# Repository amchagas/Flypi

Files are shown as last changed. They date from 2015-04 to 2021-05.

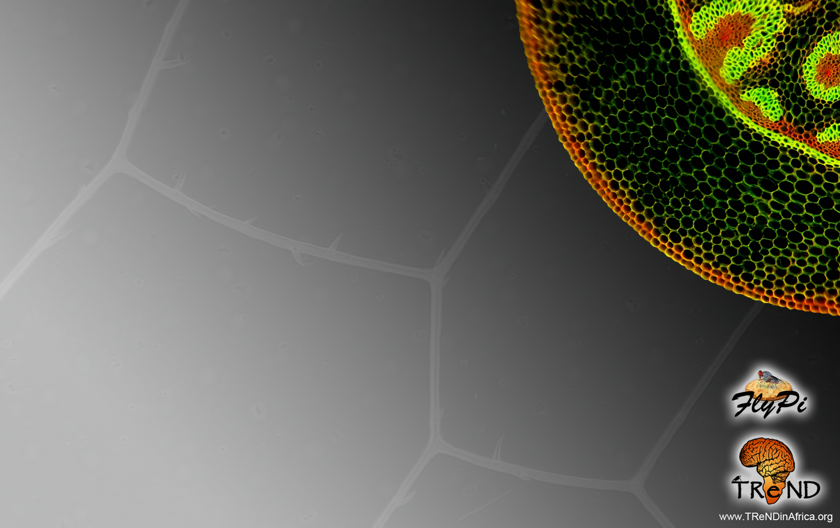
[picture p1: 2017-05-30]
logos/FlyPi_background.png

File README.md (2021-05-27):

#### Flypi - An open source, modular, affordable tool for imaging experiments.

[]()

[]()

Hi! Thanks for dropping by. This project started during one of the summer courses organized by [Trend in Africa](www.trendinafrica.org). It developed to the current state due to the efforts of many people along the way. In special Tom Baden, Lucia Prieto, and Edwin Cruz. A paper describing the system was published in [Plos Biology](http://journals.plos.org/plosbiology/article?id=10.1371/journal.pbio.2002702).

 Version 1.0 was released with the paper and can be found [here](https://github.com/amchagas/Flypi/tree/v1.0.0).

The system can be used for optical microscopy, fluorescence, behavioural tracking, optogenetics, calcium imaging and thermogenetics (see examples recorded with the system below).

#### Some samples imaged with the device:

| C.Elegans behaviour    | Drosophila Crimson  |Fluorescence ZebraFish GFP expressed in heart tissue    |
|---|---|---|
|  GCamP_ZebraFish  |Zebra Fish Transmission   |  Drosophila walking about  |

### Custom PCB

You can order the PCBs and buy the parts to assemble them through the [Kitspace page](https://kitspace.org/boards/github.com/prometheus-science/FlyPi).

#### Necessary Libraries:

LED Ring from Adafruit:
https://github.com/adafruit/Adafruit_NeoPixel

LED Matrix from Adafruit:
https://github.com/adafruit/Adafruit-LED-Backpack-Library

gpac library:
sudo apt-get update
sudo apt-get install gpac

## *.h264 conversion to *.avi:
Done via gpac. MP4BOX.

## Zipped SD Card image containing Raspian image with all things installed:

[IMAGE](https://bit.ly/flyipimg)

## Contributors ✨

Thanks goes to these wonderful people ([emoji key](https://allcontributors.org/docs/en/emoji-key)):

<!-- ALL-CONTRIBUTORS-LIST:START - Do not remove or modify this section -->
<!-- prettier-ignore -->
<table>
  <tr>
    <td align="center"><a href="http://www.openeuroscience.com">Andre Maia Chagas<br /><sub><b>Andre Maia Chagas</b></sub></a><br /><a href="https://github.com/amchagas/Flypi/commits?author=amchagas" title="Code">💻</a> <a href="#design-amchagas" title="Design">🎨</a> <a href="https://github.com/amchagas/Flypi/commits?author=amchagas" title="Documentation">📖</a></td><td align="center"><a href="https://github.com/icaven">icaven<br /><sub><b>icaven</b></sub></a><br /><a href="#design-icaven" title="Design">🎨</a></td>
    <td align="center"><a href="https://github.com/GrandeCappuccino">Edwin Cruz<br /><sub><b>Edwin Cruz</b></sub></a><br /><a href="#design-GrandeCappuccino" title="Design">🎨</a></td><td align="center"><a href="http://www.badenlab.org">Tom Baden<br /><sub><b>Tom Baden</b></sub></a><br /><a href="#design-TomBaden" title="Design">🎨</a> <a href="https://github.com/amchagas/Flypi/commits?author=TomBaden" title="Code">💻</a></td><td align="center"><a href="https://github.com/isobianin">Ihor Sobianin<br /><sub><b>Ihor Sobianin</b></sub></a><br /><a href="#design-isobianin" title="Design">🎨</a></td>
    <td align="center"><a href="https://kitspace.org">Kaspar Emanuel<br /><sub><b>Kaspar Emanuel</b></sub></a><br /><a href="https://github.com/amchagas/Flypi/commits?author=kasbah" title="Code">💻</a></td><td align="center"><a href="https://github.com/ifriad">ifriad<br /><sub><b>ifriad</b></sub></a><br /><a href="#design-ifriad" title="Design">🎨</a> <a href="https://github.com/amchagas/Flypi/commits?author=ifriad" title="Code">💻</a></td>
  </tr>
</table>

<!-- ALL-CONTRIBUTORS-LIST:END -->

This project follows the [all-contributors](https://github.com/all-contributors/all-contributors) specification. Contributions of any kind welcome!

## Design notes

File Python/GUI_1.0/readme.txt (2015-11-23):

The flypi python code is deveped in Python3 and
is now divided in the following manner:

--flypiApp.py is the code that brings different classes together into the GUI

--Run.py takes care of "executing" the flypiApp. It creates a tkinter 
root object, throws it in flypiApp, and takes care of destroying it when the 
program is terminated.

--the other files are responsible for each peripheric device used. So if the 
user wants to create code for a new peripheric device, he/she should start by 
creating a new ".py" file and with a class that contains all code to control 
that device.

---To run this new code, the user should, should call the run.py file, either 
by calling "python3 /complete/path/to/run.py" or by moving into the folder
 where the file is and then calling it from there.

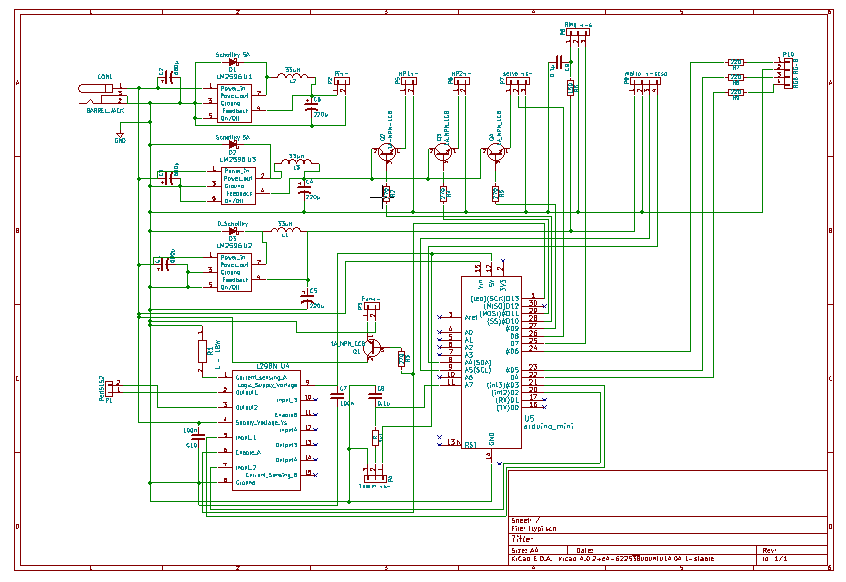
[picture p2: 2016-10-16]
PCB/flypi_pcb_kicad_smd/schematic_view.png

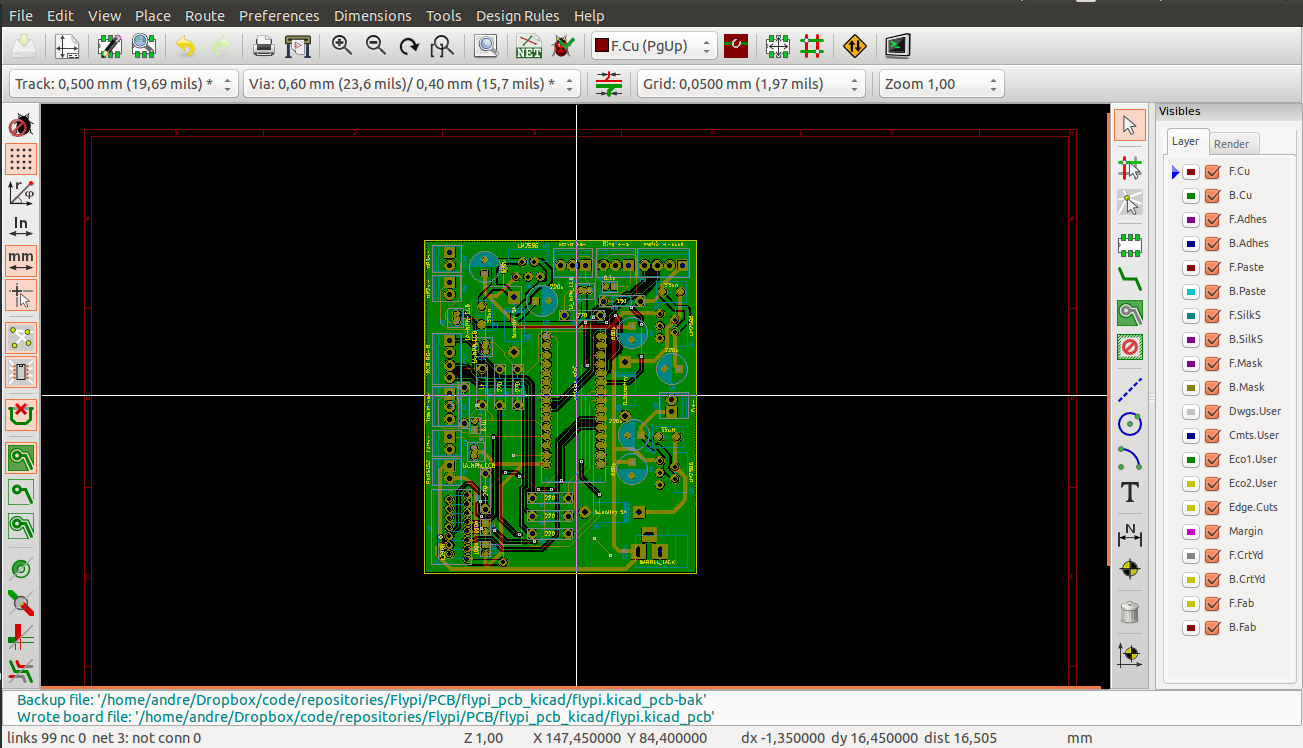
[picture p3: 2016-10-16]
PCB/flypi_pcb_kicad_smd/pcb_view.png

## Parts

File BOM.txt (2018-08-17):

Please find all necessary parts and materials for the FlyPi in: PCB/1-click-bom.tsv

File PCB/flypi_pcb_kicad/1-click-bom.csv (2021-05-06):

References | Qty | Description | Manufacturer | MPN | Manufacturer_1 | MPN_2 | Manufacturer_3 | MPN_4 | Manufacturer_5 | MPN_6 | Manufacturer_7 | MPN_8 | Digikey | Mouser | RS | Newark | Farnell
U5; | 2 | Headers 15 pin 1 row | Samtec inc | SSA-115-S-T | Samtec Inc | SSW-115-01-T-S | Amphenol | 75915-315LF |  |  |  |  | SAM1122-15-ND | 200-SSA115ST | 859-9390 | 11P7739 | 2779587
U4; | 1 | L298N Multiwatt 15 Vertical | STMicroelectronics | L298N |  |  |  |  |  |  |  |  | 497-1395-5-ND | 511L298 | 636384 | 32M1527 | 403295
U1; U2 | 2 | LM2596 5v | ITO-220 | Texas Instruments | Texas Instruments | LM2596T-5.0/NOPB |  |  |  |  |  |  | LM2596T-5.0/NOPB-ND | 926LM2596T5.0/NOPB | 5333743 | 97K3256 | 1150103
R7; R8; R9 | 3 | Resistor 220 ohm 250mW through-hole | Yageo | MFR-25FBF52-220R | TE Connectivity | CBT25J220R | TE Connectivity | CFR16J220R | Ohmite | OD221JE | Stackpole Electronics | CF14JT220R | CF14JT220RCT-ND | 279CBT25J220R | 8066376 | 21R0186 | 1265068
R2; R3; R4; R5 | 4 | Resistor 270 ohm 250mW through-hole | Stackpole Electronics | CF14JT270R | Yageo | MFR-25FBF52-220R | TE Connectivity | CFR16J270R | Ohmite | OD271JE | Kamaya | RC1/4271JB | CF14JT270RCT-ND | 791-RC1/4-271JB | 148360 | 95W5736 | 2329504
R1; | 1 | Resistor 20W TO-220 | Bourns | PWR220T-20-R500F |  |  |  |  |  |  |  |  | PWR220T-20-R500F-ND | 652PWR220T20R500F | 7962508 | 55R1098 | 2328267
Q1; Q2; Q3; Q4; Q1 | 4 | 1A NPN | ON Semiconductor/fairchild | PN2222ATF |  |  |  |  |  |  |  |  | PN2222ATFCT-ND | 512-PN2222ATF | 806-1296 | 31Y3451 | 2453811
P9; | 1 | Header 4 pin 1 row | Sullins | PPTC041LFBN-RC | Amp TE connectivity | 147721-3 |  |  |  |  |  |  | S7002-ND | 571-215297-4 | 4958543 | 98K6514 | 3419060
P10; | 1 | CONN HEADER XH TOP 4POS 2.5MM | JST | B4B-XH-A (LF)(SN) |  |  |  |  |  |  |  |  | 455-2249-ND |  | 820-1551 |  | 1516278
P4; P7; P8; | 3 | CONN HEADER XH TOP 3POS 2.5MM | JST | B3B-XH-A (LF)(SN) |  |  |  |  |  |  |  |  | 455-2248-ND |  | 8201557 | 73M9431 | 1516277
P1; P3; P5; P6; | 4 | CONN HEADER XH TOP 2POS 2.5MM | JST | B2B-XH-A (LF)(SN) |  |  |  |  |  |  |  |  | 455-2247-ND |  | 8201554P | 73M9415 | 1516276
L1; L2; | 2 | INDUCTOR 33µH Neosid MA-Bs75 | Bourns | RLB0914-330KL |  |  |  |  |  |  |  |  | RLB0914-330KL-ND | 652RLB0914330KL | 8118853 | 61J7916 | 2309242
J12; | 1 | USB A Vertical | FCI | 73725-0110BLF | Molex | 48204-0001 |  |  |  |  |  |  | 609-1041-ND | 649737250110BLF | 7710048 | 56R0832 | 2782046
D1; D3; | 2 | Diode Schottky 5A DO-201AD | Vishay | 1N5822-E3/73 | Zetex | SB5100-T |  |  |  |  |  |  | 1N5822-E3/73GICT-ND | 6251N5822E3/73 | 751-4843 | 17T8202 | 1336553
CON1; | 1 | Barrel Jack 2.1mm socket | Cliff | FC68148 DC10A | Lumberg | NEB 21 R | CUI devices | PJ-202AH | Gravitech | CON-SOCJ-2155 | Parallax | 452-00007 | CP-202AH-ND | 992CONSOCJ2155 | 5051609 | 08WX2563 | 224959
C6; C5; | 2 | CAP ALUM 220UF 20% 25V RADIAL | Panasonic | EEU-FM1E221 | Panasonic | ECA-1CM221B | Panasonic | ECE-A0GKS221 | Panasonic | EEU-EB1A221S |  |  | P12383-ND | 667ECA1CM221B | 7472036 | 70K9673 | 9451099
C2; C1; | 2 | 680µF Capacitor | Rubycon | 16ZL680MEFC10X16 | Panasonic | EEU-FC1A681 | Panasonic | EEU-FP1E681 |  |  |  |  | 1189-3978-ND | 667-EEU-FP1E681 | 7037258 | 31M6417 | 1144691
C10; C7; C8; | 3 | 100nF Capacitor Disc | Multicomp | MCFYU6104Z6 | KEMET | C052C104K5R5CA | KEMET | C052K104K5X5CA | KEMET | C052T104K5X5CS | KEMET | C321C104K5R5HA | BC1160CT-ND | 80C321C104K5R5HA | 852-3277 | 73M2154 | 2395773
1k1; | 1 | Resistor 1k 250mW through-hole | Multicomp | MF12 1K | Yageo | MFR-25FBF52-1K | RS Pro | 7077666 |  |  |  |  | 1.00KXBK-ND | 603MFR25FBF521K | 7077666 | 38K5400 | 9342400
MCU; | 1 | Arduino Mini | Arduino | A000087 | Arduino | A000005 |  |  |  |  |  |  | 1050-1001-ND | 992-ARD-NANO30 | 696-1667 | 13T9275 | 1848691
2 pin housing; | 4 | plastic housing for crimped cables 2 pins XH | JST | XHP-2 |  |  |  |  |  |  |  |  | 455-2266-ND |  | 1667314 |  | 1516264
3 pin housing; | 3 | plastic housing for crimped cables 3 pins XH | JST | XHP-3 |  |  |  |  |  |  |  |  | 455-2219-ND | 941-XHP35A0D0BD440E | 8201614 |  | 1516265
4 pin housing; | 1 | plastic housing for crimped cables 4 pins XH | JST | XHP-4 |  |  |  |  |  |  |  |  | 455-2267-ND |  | 1667316 | 74M5179 | 1516266
Crimped cable; | 21 | cables crimped with XH connectors | JST | ASXHSXH22K305 | JST | 01SXHSXH-26L 300 |  |  |  |  |  |  | 455-3241-ND |  | 820-1541
fan; | 1 | 36X36mm 5V cooling fan | Multicomp | MC36256 | NMB Technologies | 03510SS-05N-AT-00 | Sunon | MF35100V2-1000U-A99 |  |  |  |  | P19864-ND | 369-MF35100V21UA99 | 798-0754 | 23T0585 | 1924855
hdmi cable; | 1 | HDMI Cable (Raspberry to monitor) | Raspberry Pi | CPRP010-W | Tripp lite | P569-001 | Qualtek | 1721001-03 | RS pro | 801-1196 |  |  | TL1665-ND | 562-1721001-03 | 801-1196 |  | 2545201
Raspberry Pi; | 1 | Rasbperry Pi 3 | Raspberry Pi | RASPBERRYPI3-MODB-1GB | Seeed studio | 114990584 |  |  |  |  |  |  | 1690-1000-ND | 713-114990584 | 8326274 |  | 2525225
USB cable micro; | 1 | USB A to micro B | Tripp Lite | UR050-06N | rolline | 11.02.8310 | RS Pro | 121-6579 |  |  |  |  | TL1234-ND | 545-UR050-06N | 121-6579 | 68X4607 | 2444222
USB cable mini; | 1 | USB A to mini B | Tripp Lite | UR030-06N | RS-pro | 121-6572 |  |  |  |  |  |  | TL1233-ND | 545-UR030-06N | 121-6572 | 68X4592 | 2751173
LED Ring; | 1 | LED ring 12 leds | Adafruit | 1643 |  |  |  |  |  |  |  |  | 1528-1102-ND | 485-1643
RGB Led; | 1 | RGB LED 4 pins | Knight bright | WP154A4SUREQBFZGC | knight bright | L-154A4SUREQBFZGEW |  |  |  |  |  |  | 754-1615-ND | 604-WP154A4SUREQBFZG | 8614294 | 66W1972 | 2290375
SD card; | 1 | Class 10 16GB sd microsd | Apacer Memory America | AP16GMCSH10U1-B | Verbatim | 44082 |  |  |  |  |  |  | 1582-1004-ND | 908-AP16GMCSH10U1-B | 877-5557
Peltier module; | 1 | 40X40X3.8mm peltier module | CUI Inc | CP85438 | P&NTechnology | TEC1-127050 | Multicomp | MCPE1-12707AC-S | Adaptive | ET-127-14-11-RS |  |  | 102-1682-ND | 490-CP85438 | 490-1373 | 08P1446 | 1639722
heatsink; | 2 | 36X36X12 aluminum heatsink | CTS Thermal Management Products | BDN14-3CB/A01 | Fischer eletronik | ICK S 36 X 36 X 10 |  |  |  |  |  |  | 294-1101-ND | 774-BDN143CBA01 | 6744810 | 74M2393 | 1211714
UV led; | 1 | EMITTER UV 390NM 1A | LED Engin inc | LZ1-10UB00-00U4 |  |  |  |  |  |  |  |  | 1537-1137-ND |  | 9053905P
temperature sensor; | 1 | analog output | Analog devices | AD22100KTZ |  |  |  |  |  |  |  |  | AD22100KTZ-ND | 584-AD22100KTZ | 5230076 |  | 9605320
power supply; | 1 | 12V 5A output | Mean well | GSM60A12-P1J | CUI | SDI65-12-U2-P5 |  |  |  |  |  |  | 1866-2016-ND | 490-SDI65-12-U2-P5 | 7911058 | 44AC5087 | 2815822
picamera; | 1 | 5MP 12mm focal distance lens (m12 thread) | waveshare | 8193 | https://www.waveshare.com/product/mini-pc/raspberry-pi/cameras/rpi-camera-b.htm
 |  |  |  |  |  |  |  |  |  |  |  |  | CP-202AH-ND

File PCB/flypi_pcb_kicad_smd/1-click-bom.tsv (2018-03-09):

References | Qty | Description | Manufacturer | MPN | Manufacturer | MPN | Manufacturer | MPN | Manufacturer | MPN | Manufacturer | MPN | Digikey | Mouser | RS | Newark | Farnell
U1,U2,U3 | 3 | LM2596S-5 TO-263-5_TabPin3 | Texas Instruments | LM2596SX-5.0/NOPB |  |  |  |  |  |  |  |  | LM2596SX-5.0/NOPBDKR-ND | 926LM2596SX5.0NOPB |  | 85X6230 | 1496094
R9,R10,R11,R12,R13,R14 | 6 | R_1812_HandSoldering | Panasonic | ERJ-MS4SF1M0U |  |  |  |  |  |  |  |  | P17089CT-ND | 667ERJMS4SF1M0U
R8 | 1 | Resistor 1812 1k1 |  |  |  |  |  |  |  |  |  |  |  |  |  |  | 2380814
R7,R6,R5 | 3 | Resistor 1812 220ohm | Panasonic | ERJ-12ZYJ221U | Panasonic | ERJ-12YJ221U |  |  |  |  |  |  | P220WCT-ND | 667ERJ12ZYJ221U |  | 85Y7788 | 2323950
R4,R3,R2,R1 | 4 | 1812 270ohm | Royal Ohm | 1208908 | Panasonic | ERJ-12YJ271U | Panasonic | ERJ-S12J271U | Yageo | RC1218FK-07270RL | Panasonic | ERJ-U12F2700U | RC1218JK-07270RL-ND | 603RC1218JK07270RL |  |  | 2380862
Q1,Q2,Q3,Q4 | 4 | 1A NPN ECB SOT-89-3_Handsoldering | Nexperia | BCX55-10,115 |  |  |  |  |  |  |  |  | 1727-4915-6-ND | 771BCX5510115 |  | 34R2978 | 1757913RL
P9,P10 | 2 | JST_EH_S04B-EH_04x2.50mm_Angled | JST | S4B-EH (LF)(SN) | |  |  |  |  |  |  |  |  | 455-1627-ND |  |  |  | 1830721
P7,P8 | 2 | JST_EH_S03B-EH_03x2.50mm_Angled | JST | S3B-EH (LF)(SN) |  |  |  |  |  |  |  |  | 455-1626-ND |  |  | 49Y7627 | 2481438
P1,P3,P4,P5,P6 | 5 | JST_EH_S02B-EH_02x2.50mm_Angled | JST | S2B-EH (LF)(SN) |  |  |  |  |  |  |  |  | 455-1625-ND |  |  | 49Y7626 | 2481437
L298H1 | 1 | L298P HSOP-20-1EP_11.0x15.9mm | STMicroelectronics | L298P013TR |  |  |  |  |  |  |  |  | 497-3624-1-ND | 511L298PTR | 8805308P | 18AC7426 | 2762687
L1,L2,L3 | 3 | Inductor 6.3x6.3_H3 33µH | Bourns | SRR7045-330M |  |  |  |  |  |  |  |  | SRR7045-330MCT-ND | 652SRR7045330M |  |  | 2821614
J1 | 1 | USB_A_Vertical | FCI | 73725-0110BLF | ICC | 73725-0110BLF |  |  |  |  |  |  | 609-1041-ND | 649737250110BLF | 7710048 | 53K1476 | 2112380
D1,D2,D3 | 3 | D_SMB-SMC_Universal_Handsoldering Schottky 5A | Diotec | SK54
C4,C5,C6 | 3 | CP_Elec_6.3x5.3 220µ | Panasonic | EEEFPC221XAP |  |  |  |  |  |  |  |  | PCE4537CT-ND | 667EEEFPC221XAP |  | 94M6992
C10,C7,C8 | 3 | Resistor 1812 100nF
C1,C2,C3 | 3 | CP_Elec_10x10 680µ | Nichicon | UCL1C681MNL1GS |  |  |  |  |  |  |  |  | 493-3928-1-ND | 647UCL1C681MNL1GS
barrel1 | 1 | Barrel Jack CUI PJ-102AH | CUI | PJ-102AH |  |  |  |  |  |  |  |  | CP-102AH-ND | 490PJ102AH
A1 | 2 | Arduino_Nano connector 2.54 mm |  | MP70S

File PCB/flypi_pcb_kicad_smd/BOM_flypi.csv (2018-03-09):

Id | Designator | Package | Quantity | Designation | price at reichelt.de | Supplier and ref
1 | A1 | Arduino_Nano | 1 | Arduino_Nano_v3.x
2 | barrel1 | Barrel_Jack_CUI_PJ-102AH | 1 | BARREL_JACK
3 | C1,C2,C3 | CP_Elec_10x10 | 3 | 680µ
4 | C4,C5,C6 | CP_Elec_6.3x5.3 | 3 | 220µ
5 | D1,D2,D3 | D_SMB-SMC_Universal_Handsoldering | 2 | Schottky 5A
6 | L1,L2,L3 | L_6.3x6.3_H3 | 3 | 33µH
7 | L298H1 | HSOP-20-1EP_11.0x15.9mm_Pitch1.27mm_SlugUp | 1 | L298P
8 | P1,P3,P4,P5,P6 | JST_EH_S02B-EH_02x2.50mm_Angled | 5
9 | P7,P8 | JST_EH_S03B-EH_03x2.50mm_Angled | 2
10 | P9,P10 | JST_EH_S04B-EH_04x2.50mm_Angled | 2
11 | Q1,Q2,Q3,Q4 | SOT-89-3_Handsoldering | 4 | 1A NPN ECB
12 | R9,R10,R11,R12,R13,R14 | R_1812_HandSoldering | 6 | 0.1m
13 | U1,U2,U3 | TO-263-5_TabPin3 | 3 | LM2596S-5
14 | J1 | USB_A_Vertical | 1 | USB_A
15 | R4,R3,R2,R1 | R_1812_HandSoldering | 4 | 270
16 | R7,R6,R5 | R_1812_HandSoldering | 3 | 220
17 | R8 | R_1812_HandSoldering | 1 | 1k1
18 | C10,C7,C8 | C_1812_HandSoldering | 3 | 100n
19 | REF**,REF**,REF**,REF** | MountingHole_3.2mm_M3_ISO14580 | 4 | MountingHole_M3

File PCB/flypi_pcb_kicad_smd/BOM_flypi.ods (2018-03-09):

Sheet: BOM_flypi
Id | Designator | Package | Quantity | Designation | price at reichelt.de | Supplier and ref
1 | A1 | Arduino_Nano | 1 | Arduino_Nano_v3.x
2 | barrel1 | Barrel_Jack_CUI_PJ-102AH | 1 | BARREL_JACK
3 | C1,C2,C3 | CP_Elec_10x10 | 3 | 680µ
4 | C4,C5,C6 | CP_Elec_6.3x5.3 | 3 | 220µ
5 | D1,D2 | D_SMB-SMC_Universal_Handsoldering | 2 | Schottky 5A
6 | D3 | D_SMB-SMC_Universal_Handsoldering | 1 | D_Schottky
7 | L1,L2,L3 | L_6.3x6.3_H3 | 3 | 33µH
8 | L298H1 | HSOP-20-1EP_11.0x15.9mm_Pitch1.27mm_SlugUp | 1 | L298P
9 | P1 | JST_EH_S02B-EH_02x2.50mm_Angled | 1 | PeltS1S2
10 | P3 | JST_EH_S02B-EH_02x2.50mm_Angled | 1 | Fan+-
11 | P4 | JST_EH_S03B-EH_03x2.50mm_Angled | 1 | Therm +s-
12 | P5 | JST_EH_S02B-EH_02x2.50mm_Angled | 1 | HP1+-
13 | P6 | JST_EH_S02B-EH_02x2.50mm_Angled | 1 | HP2+-
14 | P7 | JST_EH_S03B-EH_03x2.50mm_Angled | 1 | servo +s-
15 | P8 | JST_EH_S03B-EH_03x2.50mm_Angled | 1 | Ring +-s
16 | P9 | JST_EH_S04B-EH_04x2.50mm_Angled | 1 | matrix +-sdsc
17 | P10 | JST_EH_S04B-EH_04x2.50mm_Angled | 1 | RGB RG-B
18 | Q1,Q3,Q4 | SOT-89-3_Handsoldering | 3 | 1A_NPN_ECB
19 | Q2 | SOT-89-3_Handsoldering | 1 | 1A-NPN-ECB
20 | R9,R10,R11,R12,R13,R14 | R_1812_HandSoldering | 6 | 0.1m
21 | U1,U2,U3 | TO-263-5_TabPin3 | 3 | LM2596S-5
22 | J1 | USB_A_Vertical | 1 | USB_A
23 | R4,R3,R2,R1 | R_1812_HandSoldering | 4 | 270
24 | R7,R6,R5 | R_1812_HandSoldering | 3 | 220
25 | R8 | R_1812_HandSoldering | 1 | 1k1
26 | C10,C7,C8 | C_1812_HandSoldering | 3 | 100n
27 | REF**,REF**,REF**,REF** | MountingHole_3.2mm_M3_ISO14580 | 4 | MountingHole_M3

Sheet: Sheet2
Id | Designator | Package | Quantity | Designation | Manufacturer Part Number
1 | A1 | Arduino_Nano connector | 2 | 2.54 mm | MP70S 1X15
2 | barrel1 | Barrel_Jack_CUI_PJ-102AH | 1 | BARREL_JACK | 75821
3 | C1,C2,C3 | CP_Elec_10x10 | 3 | 680µ | UCL1C681MNL1GS
4 | C4,C5,C6 | CP_Elec_6.3x5.3 | 3 | 220µ | EEEFPC221XAP
5 | D1,D2,D3 | D_SMB-SMC_Universal_Handsoldering | 3 | Schottky 5A | SK54
6 | L1,L2,L3 | L_6.3x6.3_H3 | 3 | 33µH | SRR7045-330M
7 | L298H1 | HSOP-20-1EP_11.0x15.9mm_Pitch1.27mm_SlugUp | 1 | L298P | L298P013TR
8 | P1,P3,P4,P5,P6 | JST_EH_S02B-EH_02x2.50mm_Angled | 5 |  | S2B-EH (LF)(SN)
9 | P7,P8 | JST_EH_S03B-EH_03x2.50mm_Angled | 2 |  | S3B-EH (LF)(SN)
10 | P9,P10 | JST_EH_S04B-EH_04x2.50mm_Angled | 2 |  | S4B-EH (LF)(SN)
11 | Q1,Q2,Q3,Q4 | SOT-89-3_Handsoldering | 4 | 1A NPN ECB | BCX55-10,115
12 | R9,R10,R11,R12,R13,R14 | R_1812_HandSoldering | 6 | 0.1m | ERJ-MS4SF1M0U
13 | U1,U2,U3 | TO-263-5_TabPin3 | 3 | LM2596S-5 | LM2596SX-5.0/NOPB
14 | J1 | USB_A_Vertical | 1 | USB_A | 73725-0110BLF
15 | R4,R3,R2,R1 | R_1812_HandSoldering | 4 | 270ohm | 1208908
16 | R7,R6,R5 | R_1812_HandSoldering | 3 | 220ohm | ERJ-12ZYJ221U
17 | R8 | R_1812_HandSoldering | 1 | 1k1 | 1206S4F1101T5E
18 | C10,C7,C8 | C_1812_HandSoldering | 3 | 100n | C1206C104K1RAC
19 | REF**,REF**,REF**,REF** | MountingHole_3.2mm_M3_ISO14580 | 4 | MountingHole_M3

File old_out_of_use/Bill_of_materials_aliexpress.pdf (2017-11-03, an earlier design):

Sheet1

details1 details2

Essential. Arduino

&

P

C

B

only ne

eded if m

odules to be

added

Common
Barrel connector | | 3A
Power supply | 12V | 5A
Custom PCB | link points to main repository page. User should go
3D printed frame | link points to main repository page. User should go t
Flat ribbon cable | 10pin | 3m colored
Screws | M3 | Head cap

Raspberry pi and cables
Capacitor | 16V | 680µF
Capacitor | 16V | 220µF
Diode | 20-60V | 3A
Inductor | 3.6A | 33µH
Screw terminal | 2pin | 6A
Switching volt reg (LM2596) | 45V | 3A
Raspberry pi 3 | Pi 2 will also work
PiCamera | V1 or V2 workbetter if it already has the lens
HDMI cable | 0.5m
USB cable | A to micro B
SD Card | 16gb | micro SD
Screws | M3 | Head cap

Arduino and cable
Arduino Nano | Atmega328
socket terminal strip | 20 pin | 2.54 spacing
USB cable | A to mini B | 0.3m

reco

m

m

ended

LED Ring
Adafruit neopixel ring | 12 LEDs
Screw terminal | 3pin | 6A
Capacitor | 16V | 680µF
Capacitor | 16V | 220µF
Diode | 20-60V | 3A
Screws | M3 | Head cap
Inductor | 3.6A | 33µH
Switching volt reg (LM2596) | 45V | 3A

optional

LED Matrix (added to Ring power circuit)
Adafruit LED matrix | 8X8 | with backpack
Screws | M3 | Head cap
Screw terminal | 2pin | 6A

Fluorescence module
LED(violet – High power) | 3.9V | 350mA
Reflective collimator | 6° | 17.5mm
Heat sink | 36X36X12
Resistor(High power) | 11W | 12Ohm

optional

Excitation filter | Roscolux #381
Emission filter | Roscolux #12
Screw terminal | 2pin | 6A
Capacitor | 16V | 680µF
Capacitor | 16V | 220µF
Diode | 20-60V | 3A
Inductor | 3.6A | 33µH
Switching volt reg (LM2596) | 45V | 3A
Screws | M3 | Head cap
Resistor | 1/4W | 270Ohm
Transisitor (BC368) | 20V | 1A

optional

Focus Servo (added to Fluorescence power circuit)
Screws | M3 | Head cap
Servo motor | 5V
Screw terminal | 3pin | 6A

Peltier module
H-Bridge (L298N) | Multiwatt 15
Fan | 5V | 40X40X20
Capacitor | 100V | 0.1µF
LED RGB | 4V | 20mA
Resistor | 1/4W | 220Ohm
Resistor | 17W | 1Ohm
Resistor | 1/4W | 270Ohm
Resistor | 1/4W | 1kOhm
Transisitor (BC368) | 20V | 1A
Peltier element | 15.4V | 6A
Screw terminal | 2pin | 6A
Heat sink | 36X36X12
Temp sensor (AD22100-KT) | TO-92 | for negative temps use AT variant

optional

Off Grid module
Lead-acid Battery | 12V | 7,2Ah
Charger | 12V | 600mA

o

ptional

likely

alre

ady

a

v

ailable

Extras
HDMI to VGA dongle | Optional
Red filter (optional) | Roscolux #19
Monitor
Keyboard & mouse set | USB
Soldering iron
Solder | 1mm
Thermal paste
Third Hand
Screw driver | 3.5mm

details3 | quantity | total* (€) | total** (€)
2,1mm int pin | 1 | 0.47 | 0.47 | 0.47
2.1mm pin | 1 | 18.65 | 18.65 | 0
| 1 | 5 | 5 | 5
| 1 | 5 | 5 | 5
AWG-28 | 1 | 1.99 | 1.99 | 0
12mm long | 2 | 0.05 | 0.1 | 0.08
Electrolitic | 1 | 0.43 | 0.43 | 0.08
Electrolitic | 1 | 0.08 | 0.08 | 0.08
Schottky | 1 | 0.18 | 0.18 | 0.03
Ferrit | 1 | 0.6 | 0.6 | 0.29
2.54mm | 1 | 0.24 | 0.24 | 0.22
TO-220-5 | 1 | 3.8 | 3.8 | 0.23
| 1 | 37.5 | 37.5 | 37.5
| 1 | 18.99 | 18.99 | 10.4
| 1 | 1.55 | 1.55 | 1.54
| 1 | 1.5 | 1.5 | 1.99
Class 10 | 1 | | | 8
6-20mm long | 20 | 0.05 | 1 | 1
| 1 | 22.9 | 22.9 | 1.98
8.5mm height | 2 | 0.27 | 0.54 | 0.11
| 1 | 1.95 | 1.95 | 0.59
122.47 74.59
| 1 | 6.71 | 6.71 | 1.6
| 1 | 0.36 | 0.36 | 0.2
Electrolitic | 1 | 0.43 | 0.43 | 0.08
Electrolitic | 1 | 0.08 | 0.08 | 0.08
Schottky | 1 | 0.18 | 0.18 | 0.03
6mm long | 1 | 0.05 | 0.05 | 0.03
Ferrit | 1 | 0.6 | 0.6 | 0.29
TO-220-5 | 1 | 3.8 | 3.8 | 0.23
12.21 2.54
blue | 1 | 10.7 | 10.7 | 3.18
6mm long | 1 | 0.05 | 0.05 | 0.03
| 1 | 0.24 | 0.24 | 0.22
10.99 3.43
130mW | 1 | 8.79 | 8.79 | 0.1
CLP17CR | 1 | 2.33 | 2.33 | 0.5
| 1 | 1.15 | 1.15 | 1.15
axial | 1 | 0.65 | 0.65

unit price (€)

| 0.001 | 10.2 | 10.2 | 0.1
| 0.001 | 10.2 | 10.2 | 0.1
| 2 | 0.24 | 0.48 | 0.44
Electrolitic | 1 | 0.43 | 0.43 | 0.08
Electrolitic | 1 | 0.08 | 0.08 | 0.08
Schottky | 1 | 0.18 | 0.18 | 0.03
Ferrit | 1 | 0.6 | 0.6 | 0.29
TO-220-5 | 1 | 3.8 | 3.8 | 0.23
6mm long | 1 | 0.05 | 0.05 | 0.03
carbon film | 1 | 0.11 | 0.11 | 0.01
0.8W | 3 | 0.08 | 0.24 | 0.02
39.29 3.16
6mm long | 1 | 0.05 | 0.05 | 0.03
cont. rotation | 1 | 6.99 | 6.99 | 3.8
| 1 | 0.36 | 0.36 | 0.2
7.35 4
| 1 | 2.4 | 2.4 | 0.93
| 1 | 7.5 | 7.5 | 2.13
Electrolitic | 2 | 0.04 | 0.08 | 0.03
4 pin | 1 | 0.58 | 0.58 | 0.11
carbon film | 3 | 0.11 | 0.33 | 0.03
Axial | 1 | 0.97 | 0.97 | 0.79
carbon film | 1 | 0.11 | 0.11 | 0.01
carbon film | 1 | 0.11 | 0.11 | 0.01
0.8W | 1 | 0.08 | 0.08 | 0.02
40X40X4.1mm | 1 | 17.1 | 17.1 | 1.98
| 4 | 0.24 | 0.96 | 0.88
| 2 | 1.15 | 2.3 | 3.2
| 1 | 3.4 | 3.4 | 3.35
35.92 13.47
TOTAL | 228.23 | 101.19
Allows the FlyPi to be | 1 | 19.8 | 19.8 | 6
charger for the lead | 1 | 8.2 | 8.2 | 2
28 8
| | Off grid TOTAL | 256.23 | 109.19

1 | 20.99 | 20.99 | 3.7
1 | 17.6 | 17.6
1 | 89.95 | 89.95
1 | 15.95 | 15.95
1 | 4.99 | 4.99
1 | 3.2 | 3.2
1 | 7.99 | 7.99
1 | 9.95 | 9.95
1 | 3.99 | 3.99
TOTAL | 174.61
Grand total | 402.84

Opportunity for substantially saving cost by sourcing elsewhere

can be sourced cheaper from overseas, or improvised from an old Laptop adapter
Estimate - prices vary widely and drop substantially when ordering in bulk
Estimate, based on material cost. If a 3D print service is required (e.g. as no 3D
This is "just" a cable supply - can be sourced from anywhere, e.g. from an old computer or printer

Can be sourced cheaper from overseas
Can be sourced slightly cheaper from overseas. Alternativelty the apporox half-priced RPi2 also works. Can be sourced cheaper from overseas, or pieced together from individual compo

Approximate and depending on configuration - see Assembly Manual

Can be sourced dramatically cheaper from overseas

Can sometimes be sourced slightly cheaper from alternative suppliers

Can be sourced cheaper from overseas

Can sometimes be sourced slighty cheaper from alternative suppliers

There are many UV LEDs available, many of which are substantially cheaper helpful to focus the light, but not essential

A full roll of filter costs 10.2 Euro, but less than 0.1% is needed A full roll of filter costs 10.2 Euro, but less than 0.1% is needed

Can be sourced cheaper from overseas

Can be sourced cheaper from alternative suppliers

Can be sourced cheaper from different suppliers. Alternatively, any old CPU fan wi

Can be sourced substantially cheaper from different suppliers

Can be sourced cheaper from different suppliers.

all prices in euros

Can be sourced signficantly cheaper from overseas Can be sourced signifcantly cheaper from overseas

all prices in euros

<

*if mostly sourced from same supplier in Germany; **if prepared to "shop around" and/or improvise

https://www.aliexpress.com/item/10pcs-Breadboard-friendly-2-1mm-DC-Barrel-Jack/32818058518.html?spm=2114.search0104.3.9.u7jJKB&ws_ab_test=searchweb0_0,searchweb201602_2_10152_10065_10151_10068_10193_10194_10308_10304_10137_10060_10302_10155_438_5360015_10https://www.aliexpress.com/item/1-PC-12-v5a-ac-100-v-to-100-v-converter-dc-12-v-adapter-5/32804289949.html?spm=2114.search0104.3.39.FDhG2y&ws_ab_test=searchweb0_0,searchweb201602_2_10152_10065_10151_10068_10193_10194_10308_10304_10137_10060_10302_10155_43https://github.com/amchagas/Flypi
https://github.com/amchagas/Flypi

https://www.aliexpress.com/item/50Pcs-M3-Alloy-Steel-Screws-Hex-Socket-Round-Head-Cap-Black-Screw-Furniture-Fastener-Bolt-M3/32773255624.html?spm=2114.search0104.3.1.SUMM5S&ws_ab_test=searchweb0_0,searchweb201602_2_10152_10065_10151_10068_10193_10194_1030

https://www.aliexpress.com/item/20-pcs-Electrolytic-Capacitors-High-Frequency-16V-680UF/1814798466.html?spm=2114.search0104.3.1.Mcotza&ws_ab_test=searchweb0_0,searchweb201602_2_10152_10065_10151_10068_10193_10194_10304_10137_10060_10302_10155_438_10154_10https://www.aliexpress.com/item/10-pcs-Electrolytic-Capacitors-High-Frequency-16V-2200UF-10X25MM/1821586609.html?spm=2114.search0104.3.17.zNurir&ws_ab_test=searchweb0_0,searchweb201602_2_10152_10065_10151_10068_10193_10194_10308_10304_10137_10060_10302_10https://www.aliexpress.com/item/10PCS-Lot-New-Original-1N5822-IN5822-Schottky-Diode-3A-40V-DIP-Wholesale-Electronic/32493170677.html?spm=2114.search0104.3.9.XafF9A&ws_ab_test=searchweb0_0,searchweb201602_2_10152_10065_10151_10068_10193_10194_10308_10304_1https://www.aliexpress.com/item/Inductor-8-10mm-33UH-frequency-ferrite-330K-0-8Amp-10-PVC-Radial-Leaded-Power-inductor-New/32760358088.html?spm=2114.search0104.3.15.cCagMV&ws_ab_test=searchweb0_0,searchweb201602_2_10152_10065_10151_10068_10193_10194_10308https://www.aliexpress.com/item/10pcs-2-Poles-2-Pin-2-54mm-PCB-Universal-Screw-Terminal-Block-Connector/32774484674.html?spm=2114.search0104.3.17.Oig9Vl&ws_ab_test=searchweb0_0,searchweb201602_2_10152_10065_10151_10068_10193_10194_10304_10137_10060_10302_https://www.aliexpress.com/item/LM2596T-5-0-LM2596-TO220-5pcs-lot/32457405052.html?spm=2114.search0104.3.59.T30gbc&ws_ab_test=searchweb0_0,searchweb201602_2_10152_10065_10151_10068_10193_10194_10308_10304_10137_10060_10302_10155_438_10154_10056_10055_1005

https://www.aliexpress.com/item/RPI-2-raspberry-pi-2-camera-Adjustable-Night-Vision-5-megapixel-OV5647-sensor-Camera-module-Support/32420453448.html?spm=2114.search0104.3.25.3VvlRs&ws_ab_test=searchweb0_0,searchweb201602_2_10152_10065_10151_10068_10193_10https://www.aliexpress.com/item/3FT-9FT-0-3M-1M-2M-3M-5M-7-5M10M-High-speed-Gold-Plated-Plug-Male/32708168897.html?spm=2114.search0104.3.1.ojxIyb&ws_ab_test=searchweb0_0,searchweb201602_2_10152_10065_10151_10068_10193_10194_10304_10137_10060_10302_10155_4https://www.aliexpress.com/item/NEW-Universal-Purple-short-20cm-Flat-Cable-USB-A-Male-to-Micro-B-Male-USB-Data/32811218645.html?spm=2114.search0104.3.8.KS32Ai&ws_ab_test=searchweb0_0,searchweb201602_2_10152_10065_10151_10068_10193_10194_10304_10137_10060_

https://www.aliexpress.com/item/Freeshipping-10PCS-Nano-3-0-controller-compatible-with-arduino-nano-CH340-USB-driver-NO-CABLE-NANO/32370018370.html?spm=2114.search0104.3.1.0nwSri&ws_ab_test=searchweb0_0,searchweb201602_2_10152_10065_10151_10068_10193_1019https://www.aliexpress.com/item/Pitch-2-54mm-2-3-4-5-6-7-8-9-10-11-12-13-14/32787280922.html?spm=2114.10010108.1000014.9.qIV5rI&traffic_analysisId=recommend_3035_null_null_null&scm=1007.13338.80878.000000000000000&pvid=0a94a4c2-fd22-4426-b37f-0ba13e005177https://www.aliexpress.com/item/High-Quality-75cm-100cm-USB-2-0-A-male-to-MINI-B-V3-5-PIN-5P/32801510782.html?spm=2114.search0104.3.25.wtOAjW&ws_ab_test=searchweb0_0,searchweb201602_2_10152_10065_10151_10068_10193_10194_10308_10304_10137_10060_10302_10155

https://www.aliexpress.com/item/10pcs-3-Poles-3-Pin-2-54mm-PCB-Universal-Screw-Terminal-Block-Connector/32776711319.html?spm=2114.search0104.3.98.aMFMyq&ws_ab_test=searchweb0_0,searchweb201602_2_10152_10065_10151_10068_10193_10194_10304_10137_10060_10302_https://www.aliexpress.com/item/20-pcs-Electrolytic-Capacitors-High-Frequency-16V-680UF/1814798466.html?spm=2114.search0104.3.1.Mcotza&ws_ab_test=searchweb0_0,searchweb201602_2_10152_10065_10151_10068_10193_10194_10304_10137_10060_10302_10155_438_10154_10https://www.aliexpress.com/item/10-pcs-Electrolytic-Capacitors-High-Frequency-16V-2200UF-10X25MM/1821586609.html?spm=2114.search0104.3.17.zNurir&ws_ab_test=searchweb0_0,searchweb201602_2_10152_10065_10151_10068_10193_10194_10308_10304_10137_10060_10302_10https://www.aliexpress.com/item/10PCS-Lot-New-Original-1N5822-IN5822-Schottky-Diode-3A-40V-DIP-Wholesale-Electronic/32493170677.html?spm=2114.search0104.3.9.XafF9A&ws_ab_test=searchweb0_0,searchweb201602_2_10152_10065_10151_10068_10193_10194_10308_10304_1https://www.aliexpress.com/item/50Pcs-M3-Alloy-Steel-Screws-Hex-Socket-Round-Head-Cap-Black-Screw-Furniture-Fastener-Bolt-M3/32773255624.html?spm=2114.search0104.3.1.SUMM5S&ws_ab_test=searchweb0_0,searchweb201602_2_10152_10065_10151_10068_10193_10194_1030https://www.aliexpress.com/item/Inductor-8-10mm-33UH-frequency-ferrite-330K-0-8Amp-10-PVC-Radial-Leaded-Power-inductor-New/32760358088.html?spm=2114.search0104.3.15.cCagMV&ws_ab_test=searchweb0_0,searchweb201602_2_10152_10065_10151_10068_10193_10194_10308https://www.aliexpress.com/item/LM2596T-5-0-LM2596-TO220-5pcs-lot/32457405052.html?spm=2114.search0104.3.59.T30gbc&ws_ab_test=searchweb0_0,searchweb201602_2_10152_10065_10151_10068_10193_10194_10308_10304_10137_10060_10302_10155_438_10154_10056_10055_1005

https://www.aliexpress.com/item/2016-New-Keyestudio-I2C-8X8-LED-Matrix-HT16K33-Lattice-Module-Black/32687211979.html?spm=2114.search0104.3.1.e0hyri&ws_ab_test=searchweb0_0,searchweb201602_2_10152_10065_10151_10068_10193_10194_10308_10304_10137_10060_10302https://www.aliexpress.com/item/50Pcs-M3-Alloy-Steel-Screws-Hex-Socket-Round-Head-Cap-Black-Screw-Furniture-Fastener-Bolt-M3/32773255624.html?spm=2114.search0104.3.1.SUMM5S&ws_ab_test=searchweb0_0,searchweb201602_2_10152_10065_10151_10068_10193_10194_1030https://www.aliexpress.com/item/10pcs-2-Poles-2-Pin-2-54mm-PCB-Universal-Screw-Terminal-Block-Connector/32774484674.html?spm=2114.search0104.3.17.Oig9Vl&ws_ab_test=searchweb0_0,searchweb201602_2_10152_10065_10151_10068_10193_10194_10304_10137_10060_10302_

https://www.aliexpress.com/item/100pcs-1W-3W-High-Power-white-warm-white-red-green-Blue-Royal-blue-660nm-LED-with/32773866977.html?spm=2114.search0104.8.3.oeDULZhttps://www.aliexpress.com/item/20pcs-Black-White-30-45-60-Degree-XP-E-XP-G-XT-E-LED-LENS-Reflector/32214132743.html?spm=2114.search0104.3.309.nLIkSr&ws_ab_test=searchweb0_0,searchweb201602_2_10152_10065_10151_10068_10193_10194_10308_10304_10137_10060_103https://www.aliexpress.com/item/Silver-Tone-Aluminum-Cooler-Radiator-Heat-Sink-Heatsink-40x40x20mm/32764361078.html?spm=2114.search0104.3.156.lYkb4w&ws_ab_test=searchweb0_0,searchweb201602_2_10152_10065_10151_10068_10193_10194_10304_10137_10060_10302_1015https://www.reichelt.de/11-Watt-axial/11W-AXIAL-12/3/index.html?&ACTION=3&LA=2&ARTICLE=1506&GROUPID=3120&artnr=11W+AXIAL+12 ?&ACTION=3&LA=2&ARTICLE=1506&GROUPID=3120&artnr=11W+AXIAL+12 https://www.reichelt.de/Blei-Vlies-Akkus-12V-Panasonic/LCR-12V-7-2P-1/3/index.html?ACTION=3&LA=5&ARTICLE=26559&GROUPID=4234&artnr=LCR-12V+7%2C2P-1https://www.reichelt.de/Ladegeraete-fuer-Bleiakkus/LADER-AS/3/index.html?ACTION=3&LA=5&ARTICLE=115306&GROUPID=4193&artnr=LADER+AShttps://www.rosco.com/uk/german/filters/roscolux.cfm
https://www.rosco.com/uk/german/filters/roscolux.cfmhttps://www.aliexpress.com/item/10pcs-2-Poles-2-Pin-2-54mm-PCB-Universal-Screw-Terminal-Block-Connector/32774484674.html?spm=2114.search0104.3.17.Oig9Vl&ws_ab_test=searchweb0_0,searchweb201602_2_10152_10065_10151_10068_10193_10194_10304_10137_10060_10302_https://www.aliexpress.com/item/20-pcs-Electrolytic-Capacitors-High-Frequency-16V-680UF/1814798466.html?spm=2114.search0104.3.1.Mcotza&ws_ab_test=searchweb0_0,searchweb201602_2_10152_10065_10151_10068_10193_10194_10304_10137_10060_10302_10155_438_10154_10https://www.aliexpress.com/item/10-pcs-Electrolytic-Capacitors-High-Frequency-16V-2200UF-10X25MM/1821586609.html?spm=2114.search0104.3.17.zNurir&ws_ab_test=searchweb0_0,searchweb201602_2_10152_10065_10151_10068_10193_10194_10308_10304_10137_10060_10302_10https://www.aliexpress.com/item/10PCS-Lot-New-Original-1N5822-IN5822-Schottky-Diode-3A-40V-DIP-Wholesale-Electronic/32493170677.html?spm=2114.search0104.3.9.XafF9A&ws_ab_test=searchweb0_0,searchweb201602_2_10152_10065_10151_10068_10193_10194_10308_10304_1https://www.aliexpress.com/item/Inductor-8-10mm-33UH-frequency-ferrite-330K-0-8Amp-10-PVC-Radial-Leaded-Power-inductor-New/32760358088.html?spm=2114.search0104.3.15.cCagMV&ws_ab_test=searchweb0_0,searchweb201602_2_10152_10065_10151_10068_10193_10194_10308https://www.aliexpress.com/item/LM2596T-5-0-LM2596-TO220-5pcs-lot/32457405052.html?spm=2114.search0104.3.59.T30gbc&ws_ab_test=searchweb0_0,searchweb201602_2_10152_10065_10151_10068_10193_10194_10308_10304_10137_10060_10302_10155_438_10154_10056_10055_1005https://www.aliexpress.com/item/50Pcs-M3-Alloy-Steel-Screws-Hex-Socket-Round-Head-Cap-Black-Screw-Furniture-Fastener-Bolt-M3/32773255624.html?spm=2114.search0104.3.1.SUMM5S&ws_ab_test=searchweb0_0,searchweb201602_2_10152_10065_10151_10068_10193_10194_1030https://www.aliexpress.com/item/100PCS-1-4W-270-ohm-resistor-1-ROHS1-4w-270R-ohm-Metal-Film-Resistors-0/32689112935.html?spm=2114.search0104.3.1.6BUaVe&ws_ab_test=searchweb0_0,searchweb201602_2_10152_10065_10151_10068_10193_10194_10308_10304_10137_10060_1https://www.aliexpress.com/item/100PCS-Transistor-BC639-1A-80V-NPN-transistor-TO-92-DIP/32430350812.html?spm=2114.search0104.3.52.Iurn3U&ws_ab_test=searchweb0_0,searchweb201602_2_10152_10065_10151_10068_10193_10194_10308_10304_10137_10060_10302_10155_438_

https://www.aliexpress.com/item/50Pcs-M3-Alloy-Steel-Screws-Hex-Socket-Round-Head-Cap-Black-Screw-Furniture-Fastener-Bolt-M3/32773255624.html?spm=2114.search0104.3.1.SUMM5S&ws_ab_test=searchweb0_0,searchweb201602_2_10152_10065_10151_10068_10193_10194_1030https://www.aliexpress.com/item/RCmall-Feetech-FS90R-Servo-360-Degree-Continuous-Rotation-Micro-RC-Quadcopter-Servo-For-RC-Car-Boat/32783328217.html?spm=2114.search0104.3.9.BZkPOx&ws_ab_test=searchweb0_0,searchweb201602_2_10152_10065_10151_10068_10193_101https://www.aliexpress.com/item/10pcs-3-Poles-3-Pin-2-54mm-PCB-Universal-Screw-Terminal-Block-Connector/32776711319.html?spm=2114.search0104.3.98.aMFMyq&ws_ab_test=searchweb0_0,searchweb201602_2_10152_10065_10151_10068_10193_10194_10304_10137_10060_10302_

https://www.aliexpress.com/item/5PCS-IC-L298-L298N-ZIP-15-IC-DRIVER-FULL-DUAL-15MULTIWATT-GOOD-QUANLITY/32649183724.html?spm=2114.search0104.3.17.Q5rLsI&ws_ab_test=searchweb0_0,searchweb201602_2_10152_10065_10151_10068_10193_10194_10308_10304_10137_10060_https://www.aliexpress.com/item/4010-fan-2pins-40mm-40mmx40mmx10mm-4cm-graphics-card-fan-cooling-fan-DC-24V-24V-4010-2P/32705615199.html?spm=2114.search0104.3.2.ikw6Zk&ws_ab_test=searchweb0_0,searchweb201602_2_10152_10065_10151_10068_10193_10194_10308_103https://www.aliexpress.com/item/50pcs-0-1uF-0-1-uF-104-50V-Mono-Monolithic-Capacitors/32816477062.html?spm=2114.search0104.3.26.wsvv2i&ws_ab_test=searchweb0_0,searchweb201602_2_10152_10065_10151_10068_10193_10194_10308_10304_10137_10060_10302_10155_438_10https://www.aliexpress.com/item/10pcs-lot-5mm-RGB-LED-Common-Cathode-4pin-Red-Green-Blue-LED-Round-Tricolor-LED-Light/32601543257.html?spm=2114.search0104.3.18.pWpXpO&ws_ab_test=searchweb0_0,searchweb201602_2_10152_10065_10151_10068_10193_10194_10308_1030https://www.aliexpress.com/item/100PCS-LOT-1-4W-220-ohm-resistor-1-ROHS1-4w-220R-ohm-Metal-Film-Resistors/32689231347.html?spm=2114.search0104.3.2.enbSOD&ws_ab_test=searchweb0_0,searchweb201602_2_10152_10065_10151_10068_10193_10194_10308_10304_10137_10060https://www.aliexpress.com/item/High-Quality-10Pcs-1-ohm-R-1ohm-1R-20W-Cement-Ceramic-Power-Horizontal-Resistor-Resistance-Free/1923204405.html?spm=2114.search0104.3.15.u5AIa6&ws_ab_test=searchweb0_0,searchweb201602_2_10152_10065_10151_10068_10193_10194_1https://www.aliexpress.com/item/100PCS-1-4W-270-ohm-resistor-1-ROHS1-4w-270R-ohm-Metal-Film-Resistors-0/32689112935.html?spm=2114.search0104.3.1.6BUaVe&ws_ab_test=searchweb0_0,searchweb201602_2_10152_10065_10151_10068_10193_10194_10308_10304_10137_10060_1https://www.aliexpress.com/item/1LOT-100PCS-Metal-Film-Axial-Resistors-1Kohm-1001-1-1-4W-1000ohm-0-25W-electronic-components/32526546113.html?spm=2114.search0104.3.25.4e4kaC&ws_ab_test=searchweb0_0,searchweb201602_2_10152_10065_10151_10068_10193_10194_103https://www.aliexpress.com/item/100PCS-Transistor-BC639-1A-80V-NPN-transistor-TO-92-DIP/32430350812.html?spm=2114.search0104.3.52.Iurn3U&ws_ab_test=searchweb0_0,searchweb201602_2_10152_10065_10151_10068_10193_10194_10308_10304_10137_10060_10302_10155_438_https://www.aliexpress.com/item/Free-shipping-5pcs-lot-TEC1-12705-Thermoelectric-Cooler-Peltier-12705-12V-5A-Cells-TEC12705-Peltier-Elemente/32275121350.html?spm=2114.search0104.3.9.9Wx8Wt&ws_ab_test=searchweb0_0,searchweb201602_2_10152_10065_10151_10068_https://www.aliexpress.com/item/10pcs-2-Poles-2-Pin-2-54mm-PCB-Universal-Screw-Terminal-Block-Connector/32774484674.html?spm=2114.search0104.3.17.Oig9Vl&ws_ab_test=searchweb0_0,searchweb201602_2_10152_10065_10151_10068_10193_10194_10304_10137_10060_10302_https://www.aliexpress.com/item/Aluminum-alloy-35-35-10MM-High-quality-heat-sink-Main-heat-sink-North-and-south-bridge/32425561394.html?spm=2114.search0104.3.188.v7LOmw&ws_ab_test=searchweb0_0,searchweb201602_2_10152_10065_10151_10068_10193_10194_10308_10https://www.aliexpress.com/item/AD22100KTZ-AD22100-AD-TO-92-IC-Free-Shipping/1894932812.html?spm=2114.search0104.3.8.5NtGmy&ws_ab_test=searchweb0_0,searchweb201602_2_10152_10065_10151_10068_10193_10194_10308_10304_10137_10060_10302_10155_438_10154_10056_1https://www.aliexpress.com/item/Retail-White-1pcs-1080P-HDMI-to-VGA-Converter-Adapter-Dongle-with-3-5mm-Audio-for-Laptop/32676772603.html?ws_ab_test=searchweb0_0,searchweb201602_2_10152_10065_10151_10068_10193_10084_10308_10083_10080_10082_10081_10110_10303_10137_10111_10302_10060_10176_10112_10113_10155_10114_10154_438_10056_10055_10054_10310_10182_10059_10184_100031_10099_10078_10079_10210_10103_10073_10102_5360020_10052_10053_10142_10107_10050_10051,searchweb201603_1,ppcSwitch_3&btsid=e4a3ec85-8abe-4688-be38-01f0686645b5&algo_expid=a14bf3af-af23-4a86-af64-eff0c30cad90-5&algo_pvid=a14bf3af-af23-4a86-af64-eff0c30cad90 https://www.rosco.com/uk/german/filters/roscolux.cfm
https://www.reichelt.de/HANNS-G-HE225DPB/3/index.html?&ACTION=3&LA=446&ARTICLE=130197&artnr=HANNS-G+HE225DPB&SEARCH=pc+monitore
http://www.reichelt.de/Keyboard-Mouse-Sets/CHERRY-JD-0800DE/3/index.html?&ACTION=3&LA=2&ARTICLE=154150&GROUPID=6267&artnr=CHERRY+JD-0800DE
https://www.reichelt.de/KOLBEN-FP-30/3/index.html?&ACTION=3&LA=446&ARTICLE=89497&artnr=KOLBEN+FP+30&SEARCH=soldering+ironhttps://www.reichelt.de/Solder/LZ-FE-1-0-100/3/index.html?&ACTION=3&LA=2&ARTICLE=30439&GROUPID=557&artnr=LZ+FE+1%2C0+100https://www.reichelt.de/TG-WLPA-015/3/index.html?&ACTION=3&LA=446&ARTICLE=156447&artnr=TG-WLPA-015&SEARCH=thermal+pastehttps://www.reichelt.de/Holders-Vices/HALTER-ZD-10MB/3/index.html?&ACTION=3&LA=5700&ARTICLE=145605&GROUPID=4143&artnr=HALTER+ZD-10MBhttps://www.reichelt.de/Standard-soft-finish/WIHA-302-3-5/3/index.html?&ACTION=3&LA=2&ARTICLE=28685&GROUPID=561&artnr=WIHA+302-3%2C5https://www.reichelt.de/Blei-Vlies-Akkus-12V-Panasonic/LCR-12V-7-2P-1/3/index.html?ACTION=3&LA=5&ARTICLE=26559&GROUPID=4234&artnr=LCR-12V+7%2C2P-1

or maybe this would work https://www.reichelt.de/11-Watt-axial/11W-AXIAL-12/3/index.html?&ACTION=3&LA=2&ARTICLE=1506&GROUPID=3120&artnr=11W+AXIAL+12

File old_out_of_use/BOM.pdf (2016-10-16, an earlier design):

Sheet1

details1 | details2 | details3 | quantity | unit price
Common
Barrel connector | | 3A | 2,1mm int pin | 1 | 0.47
Power supply | 12V | 5A | 2.1mm pin | 1 | 18.65
Custom PCB | | | | 1 | 5
3D printed frame | | | | 1 | 5
Flat ribbon cable | 10pin | 3m colored | AWG-28 | 1 | 1.99

Raspberry pi module
Capacitor | 16V | 680µF | Electrolitic | 1 | 0.43
Capacitor | 16V | 220µF | Electrolitic | 1 | 0.08
Diode | 20-60V | 3A | Schottky | 1 | 0.18
Inductor | 3.6A | 33µH | Ferrit | 1 | 0.6
Screw terminal | 2pin | 6A | | 1 | 0.24
Switching volt reg (LM2596) | 45V | 3A | TO-220-5 | 1 | 3.8
Raspberry pi 3 | Pi 2 will also work | 1 | 37.5
HDMI cable | 0.5m | | | 1 | 1.55
USB cable | A to micro B | | | 1 | 1.5
Screws | M3 | Head cap | 6mm long | 4 | 0.05

Arduino module
Arduino Nano | Atmega328 | | | 1 | 22.9
socket terminal strip | 20 pin | 2.54 spacing 8.5mm height | 2 | 0.27
USB cable | A to mini B | 0.3m | | 1 | 1.95

Peltier module
H-Bridge (L298N) | Multiwatt 15 | | | 1 | 2.4
Fan | 5V | 40X40X20 | | 1 | 7.5
Capacitor | 100V | 0.1µF | Electrolitic | 2 | 0.04
LED RGB | 4V | 20mA | 4 pin | 1 | 0.58
Resistor | 1/4W | 220Ohm | carbon film | 3 | 0.11
Resistor | 17W | 1Ohm | Axial | 1 | 0.97
Resistor | 1/4W | 270Ohm | carbon film | 1 | 0.11
Resistor | 1/4W | 1kOhm | carbon film | 1 | 0.11
Transisitor (BC368) | 20V | 1A | 0.8W | 1 | 0.08
Peltier element | 15.4V | 6A | 40X40X4.1mm | 1 | 17.1
Screw terminal | 2pin | 6A | | 4 | 0.24
Heat sink | 36X36X12 | | | 2 | 1.15
Temp sensor (AD22100-KT) | TO-92 | for negative temps use AT va | 1 | 3.4

Ring + Matrix
Capacitor | 16V | 680µF | Electrolitic | 1 | 0.43
Capacitor | 16V | 220µF | Electrolitic | 1 | 0.08
Diode | 20-60V | 3A | Schottky | 1 | 0.18
Inductor | 3.6A | 33µH | Ferrit | 1 | 0.6
Switching volt reg (LM2596) | 45V | 3A | TO-220-5 | 1 | 3.8
Screw terminal | 3pin | 6A | | 1 | 0.36
Screw terminal | 2pin | 6A | | 1 | 0.24
Adafruit neopixel ring | 12 LEDs | | | 1 | 6.71
Adafruit LED matrix | 8X8 | with backpackblue | 1 | 10.7

Power LEDs + Servo
Capacitor | 16V | 680µF | Electrolitic | 1 | 0.43
Capacitor | 16V | 220µF | Electrolitic | 1 | 0.08
Diode | 20-60V | 3A | Schottky | 1 | 0.18
Inductor | 3.6A | 33µH | Ferrit | 1 | 0.6
Switching volt reg (LM2596) | 45V | 3A | TO-220-5 | 1 | 3.8
Resistor | 1/4W | 270Ohm | carbon film | 1 | 0.11
Transisitor (BC368) | 20V | 1A | 0.8W | 3 | 0.08
LED(violet – High power) | 3.9V | 350mA | 130mW | 1 | 8.79
Resistor(High power) | 11W | 12Ohm | axial | 1 | 0.65
Reflective collimator | 6° | 17.5mm | CLP17CR | 1 | 2.33
Heat sink | 36X36X12 | | | 1 | 1.15
Excitation filter | Roscolux #381 | 1 | 10.2
Emission filter | Roscolux #12 | | | 1 | 10.2
Servo motor | 5V | | cont. rotation | 1 | 6.99
Screw terminal | 3pin | 6A | | 1 | 0.36
Screw terminal | 2pin | 6A | | 2 | 0.24

TOTAL

Extras
HDMI to VGA dongle | Optional | 1 | 20.99
Red filter (optional) | Roscolux #19 | 1 | 17.6
Monitor | | 1 | 89.95
Keyboard & mouse set | USB | 1 | 15.95
Soldering iron | | 1 | 4.99
Solder | 1mm | 1 | 3.2
Thermal paste | | 1 | 7.99
Third Hand | | 1 | 9.95
Screw driver | 3.5mm | 1 | 3.99

TOTAL

| | | Grand total

total

0.47
18.65
5
5
1.99

0.43
0.08
0.18
0.6
0.24
3.8
37.5
1.55
1.5
0.2

22.9
0.54
1.95

2.4
7.5
0.08
0.58
0.33
0.97
0.11
0.11
0.08
17.1
0.96
2.3
3.4

0.43
0.08
0.18
0.6
3.8
0.36
0.24
6.71
10.7

https://www.reichelt.de/DC-Jacks/LUM-NEB-21R/3/index.html?&ACTION=3&LA=2&ARTICLE=116262&GROUPID=3258&artnr=LUM+NEB+21Rhttps://www.reichelt.de/Power-Supplies-Fixed-Voltage/MW-GST60A12/3/index.html?&ACTION=3&LA=2&ARTICLE=169684&GROUPID=4950&artnr=MW+GST60A12https://github.com/amchagas/Flypi/tree/development/PCB
https://github.com/amchagas/Flypi/tree/development/3D_print_fileshttps://www.reichelt.de/Flachbandkabel/AWG-28-10F-3M/3/index.html?ACTION=3&GROUPID=3328&ARTICLE=47668&OFFSET=16&SID=12V0KkLawQATQAAHaiTrQ76eddfec27d96e4abaa567a74d209b7b&LANGUAGE=EN

https://www.reichelt.de/Elkos-radial-105-C-1000-5000h/RAD-FC-680-16/3/index.html?&ACTION=3&LA=5700&ARTICLE=84685&GROUPID=4000&artnr=RAD+FC+680%2F16https://www.reichelt.de/Elkos-radial-85-C/RAD-220-63/3/index.html?&ACTION=3&LA=5700&ARTICLE=15121&GROUPID=3143&artnr=RAD+220%2F63https://www.reichelt.de/SB-SKE-4F-Dioden/SB-330/3/index.html?&ACTION=3&LA=5700&ARTICLE=16039&GROUPID=2991&artnr=SB+330https://www.reichelt.de/Fest-Induktivitaeten-radial/L-09HCP-33-/3/index.html?ACTION=3&GROUPID=3180&ARTICLE=138657&OFFSET=16&SID=11V0QcSawQATMAAEmsvA88c90efb72bf42bc26df1c2bd134cc523&LANGUAGE=ENhttps://www.reichelt.de/Screw-terminals/AKL-059-02/3/index.html?&ACTION=3&LA=5700&ARTICLE=36598&GROUPID=7246&artnr=AKL+059-02https://www.reichelt.de/ICs-LM-2000-LM-25576/LM-2596-T5-0/3/index.html?&ACTION=3&LA=5700&ARTICLE=109365&GROUPID=5466&artnr=LM+2596+T5%2C0http://www.reichelt.de/RASPBERRY-PI-3/3/index.html?&ACTION=3&LA=446&ARTICLE=164977&artnr=RASPBERRY+PI+3&SEARCH=raspberry+pi3http://www.reichelt.de/A-V-Cables-HDMI-mini-micro-HDMI-/AK-HDMI-0-50G-ET/3/index.html?&ACTION=3&LA=2&ARTICLE=141813&GROUPID=3615&artnr=AK+HDMI+0%2C50G+EThttp://www.reichelt.de/USB-Cables/AK-676-AB/3/index.html?&ACTION=3&LA=2&ARTICLE=74221&GROUPID=6099&artnr=AK+676-ABhttp://www.screwsandmore.de/en/50-pcs-DIN-912-A2-M3X6.html

https://www.reichelt.de/ARDUINO-NANO/3/index.html?&ACTION=3&LA=446&ARTICLE=142943&artnr=ARDUINO+NANO&SEARCH=arduino+nanohttps://www.reichelt.de/Buchsenleisten/BL-1X20G8-2-54/3/index.html?&ACTION=3&LA=5700&ARTICLE=51827&GROUPID=3221&artnr=BL+1X20G8+2%2C54http://www.reichelt.de/USB-Cables/DELOCK-83178/3/index.html?&ACTION=3&LA=2&ARTICLE=163118&GROUPID=6099&artnr=DELOCK+83178

https://www.reichelt.de/L-298/3/index.html?&ACTION=3&LA=446&ARTICLE=9667&artnr=L+298&SEARCH=l298nhttps://www.conrad.de/de/axialluefter-5-vdc-1189-mh-l-x-b-x-h-40-x-40-x-10-mm-sunon-mb40100v2-0000-a99-183719.htmlhttps://www.reichelt.de/Elkos-radial-85-C/RAD-0-1-100/3/index.html?&ACTION=3&LA=5700&ARTICLE=15085&GROUPID=3143&artnr=RAD+0%2C1%2F100https://www.reichelt.de/LED-LL-5-8000RGB/3/index.html?&ACTION=3&LA=446&ARTICLE=156358&artnr=LED+LL+5-8000RGB&SEARCH=rgb+ledhttps://www.reichelt.de/1-4W-5-100-Ohm-910-Ohm/1-4W-220/3/index.html?&ACTION=3&LA=5700&ARTICLE=1382&GROUPID=3064&artnr=1%2F4W+220https://www.reichelt.de/17-Watt-axial/17W-AXIAL-1-0/3/index.html?&ACTION=3&LA=5700&ARTICLE=1629&GROUPID=3122&artnr=17W+AXIAL+1%2C0https://www.reichelt.de/1-4W-5-100-Ohm-910-Ohm/1-4W-270/3/index.html?&ACTION=3&LA=5700&ARTICLE=1390&GROUPID=3064&artnr=1%2F4W+270https://www.reichelt.de/1-4W-5-1-0-k-Ohm-9-1-k-Ohm/1-4W-1-0K/3/index.html?&ACTION=3&LA=2&ARTICLE=1315&GROUPID=3065&artnr=1%2F4W+1%2C0Khttps://www.reichelt.de/BC-Transistors/BC-368/3/index.html?&ACTION=3&LA=5700&ARTICLE=4992&GROUPID=7206&artnr=BC+368https://www.reichelt.de/TEC1-127-05/3/index.html?&ACTION=3&LA=446&ARTICLE=149024&artnr=TEC1+127+05&SEARCH=peltierhttps://www.reichelt.de/Screw-terminals/AKL-059-02/3/index.html?&ACTION=3&LA=5700&ARTICLE=36598&GROUPID=7246&artnr=AKL+059-02https://www.reichelt.de/Heat-Sinks-PCB-mounting/V-ICK-PGA36X36/3/index.html?&ACTION=3&LA=2&ARTICLE=100978&GROUPID=4621&artnr=V+ICK+PGA36X36https://www.reichelt.de/AD-22100-KT/3/index.html?&ACTION=3&LA=446&ARTICLE=39279&artnr=AD+22100+KT&SEARCH=ad22100kt

https://www.reichelt.de/Elkos-radial-105-C-1000-5000h/RAD-FC-680-16/3/index.html?&ACTION=3&LA=5700&ARTICLE=84685&GROUPID=4000&artnr=RAD+FC+680%2F16https://www.reichelt.de/Elkos-radial-85-C/RAD-220-63/3/index.html?&ACTION=3&LA=5700&ARTICLE=15121&GROUPID=3143&artnr=RAD+220%2F63https://www.reichelt.de/SB-SKE-4F-Dioden/SB-330/3/index.html?&ACTION=3&LA=5700&ARTICLE=16039&GROUPID=2991&artnr=SB+330https://www.reichelt.de/Fest-Induktivitaeten-radial/L-09HCP-33-/3/index.html?ACTION=3&GROUPID=3180&ARTICLE=138657&OFFSET=16&SID=11V0QcSawQATMAAEmsvA88c90efb72bf42bc26df1c2bd134cc523&LANGUAGE=ENhttps://www.reichelt.de/ICs-LM-2000-LM-25576/LM-2596-T5-0/3/index.html?&ACTION=3&LA=5700&ARTICLE=109365&GROUPID=5466&artnr=LM+2596+T5%2C0https://www.reichelt.de/Screw-terminals/AKL-059-03/3/index.html?&ACTION=3&LA=2&ARTICLE=36599&GROUPID=7246&artnr=AKL+059-03https://www.reichelt.de/Screw-terminals/AKL-059-02/3/index.html?&ACTION=3&LA=5700&ARTICLE=36598&GROUPID=7246&artnr=AKL+059-02
https://www.adafruit.com/product/1643
https://www.adafruit.com/products/1052

0.43
0.08
0.18
0.6
3.8
0.11
0.24
8.79
0.65
2.33
1.15
10.2
10.2
6.99
0.36
0.48

208.19 all prices in euros and most items from the same distributor – which is not the cheapest one available.

20.99
17.6
89.95
15.95
4.99
3.2
7.99
9.95
3.99

174.61

382.8

https://www.reichelt.de/Elkos-radial-105-C-1000-5000h/RAD-FC-680-16/3/index.html?&ACTION=3&LA=5700&ARTICLE=84685&GROUPID=4000&artnr=RAD+FC+680%2F16https://www.reichelt.de/Elkos-radial-85-C/RAD-220-63/3/index.html?&ACTION=3&LA=5700&ARTICLE=15121&GROUPID=3143&artnr=RAD+220%2F63https://www.reichelt.de/SB-SKE-4F-Dioden/SB-330/3/index.html?&ACTION=3&LA=5700&ARTICLE=16039&GROUPID=2991&artnr=SB+330https://www.reichelt.de/Fest-Induktivitaeten-radial/L-09HCP-33-/3/index.html?ACTION=3&GROUPID=3180&ARTICLE=138657&OFFSET=16&SID=11V0QcSawQATMAAEmsvA88c90efb72bf42bc26df1c2bd134cc523&LANGUAGE=ENhttps://www.reichelt.de/ICs-LM-2000-LM-25576/LM-2596-T5-0/3/index.html?&ACTION=3&LA=5700&ARTICLE=109365&GROUPID=5466&artnr=LM+2596+T5%2C0https://www.reichelt.de/1-4W-5-100-Ohm-910-Ohm/1-4W-270/3/index.html?&ACTION=3&LA=5700&ARTICLE=1390&GROUPID=3064&artnr=1%2F4W+270https://www.reichelt.de/BC-Transistors/BC-368/3/index.html?&ACTION=3&LA=5700&ARTICLE=4992&GROUPID=7206&artnr=BC+368
http://www.roithner-laser.com/led_highsingle_hexagonal.html But maybe this would work?
https://www.reichelt.de/11-Watt-axial/11W-AXIAL-12/3/index.html?&ACTION=3&LA=2&ARTICLE=1506&GROUPID=3120&artnr=11W+AXIAL+12 ?&ACTION=3&LA=2&ARTICLE=1506&GROUPID=3120&artnr=11W+AXIAL+12 or maybe this would work https://www.reichelt.de/11-Watt-axial/11W-AXIAL-12/3/index.html?&ACTION=3&LA=2&ARTICLE=1506&GROUPID=3120&artnr=11W+AXIAL+12http://www.roithner-laser.com/led_highoptic.html
https://www.reichelt.de/Heat-Sinks-PCB-mounting/V-ICK-PGA36X36/3/index.html?&ACTION=3&LA=2&ARTICLE=100978&GROUPID=4621&artnr=V+ICK+PGA36X36https://www.rosco.com/uk/german/filters/roscolux.cfm
https://www.rosco.com/uk/german/filters/roscolux.cfmhttps://www.conrad.de/de/modelcraft-mini-servo-y-3009-analog-servo-getriebe-material-kunststoff-stecksystem-jr-209089.htmlhttps://www.reichelt.de/Screw-terminals/AKL-059-03/3/index.html?&ACTION=3&LA=2&ARTICLE=36599&GROUPID=7246&artnr=AKL+059-03https://www.reichelt.de/Screw-terminals/AKL-059-02/3/index.html?&ACTION=3&LA=5700&ARTICLE=36598&GROUPID=7246&artnr=AKL+059-02

https://www.conrad.de/de/manhattan-hdmi-auf-vga-konverter-1284618.html
https://www.rosco.com/uk/german/filters/roscolux.cfmhttps://www.reichelt.de/HANNS-G-HE225DPB/3/index.html?&ACTION=3&LA=446&ARTICLE=130197&artnr=HANNS-G+HE225DPB&SEARCH=pc+monitorehttp://www.reichelt.de/Keyboard-Mouse-Sets/CHERRY-JD-0800DE/3/index.html?&ACTION=3&LA=2&ARTICLE=154150&GROUPID=6267&artnr=CHERRY+JD-0800DEhttps://www.reichelt.de/KOLBEN-FP-30/3/index.html?&ACTION=3&LA=446&ARTICLE=89497&artnr=KOLBEN+FP+30&SEARCH=soldering+ironhttps://www.reichelt.de/Solder/LZ-FE-1-0-100/3/index.html?&ACTION=3&LA=2&ARTICLE=30439&GROUPID=557&artnr=LZ+FE+1%2C0+100https://www.reichelt.de/TG-WLPA-015/3/index.html?&ACTION=3&LA=446&ARTICLE=156447&artnr=TG-WLPA-015&SEARCH=thermal+pastehttps://www.reichelt.de/Holders-Vices/HALTER-ZD-10MB/3/index.html?&ACTION=3&LA=5700&ARTICLE=145605&GROUPID=4143&artnr=HALTER+ZD-10MBhttps://www.reichelt.de/Standard-soft-finish/WIHA-302-3-5/3/index.html?&ACTION=3&LA=2&ARTICLE=28685&GROUPID=561&artnr=WIHA+302-3%2C5

But maybe this would work? http://www.reichelt.de/SMD-LEDs-Standard/2/index.html?&ACTION=2&LA=2&GROUP=A5381&GROUPID=3035&START=0&OFFSET=500&SHOW=1https://www.reichelt.de/11-Watt-axial/11W-AXIAL-12/3/index.html?&ACTION=3&LA=2&ARTICLE=1506&GROUPID=3120&artnr=11W+AXIAL+12

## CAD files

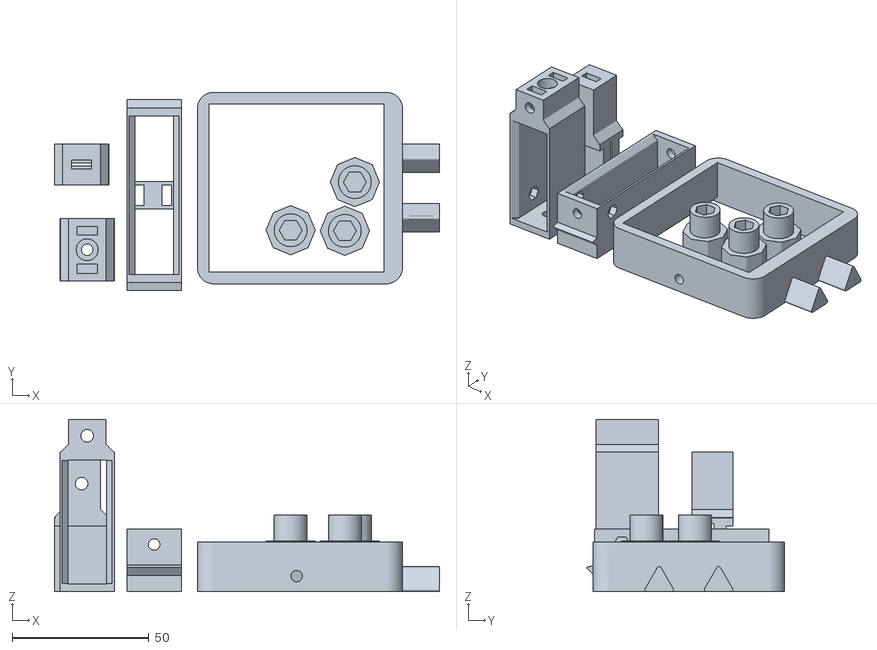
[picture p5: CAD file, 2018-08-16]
3D_print_files/v2.0/plates/Manipulator_complete.stl
140.7 x 72.5 x 63.0

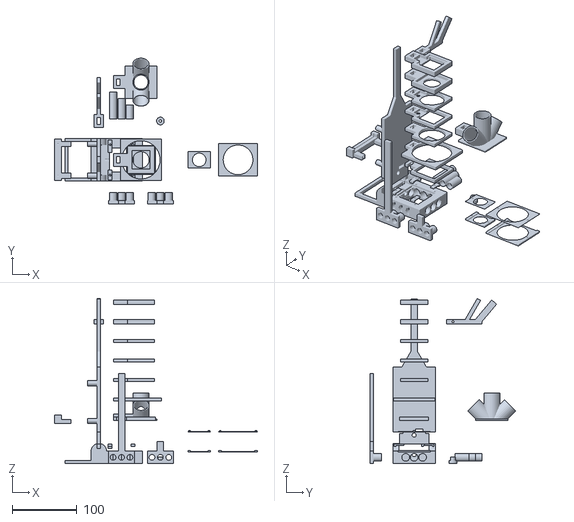
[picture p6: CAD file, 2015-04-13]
3D_print_files/FlyPi_v20.stl
313.5 x 225.1 x 254.8

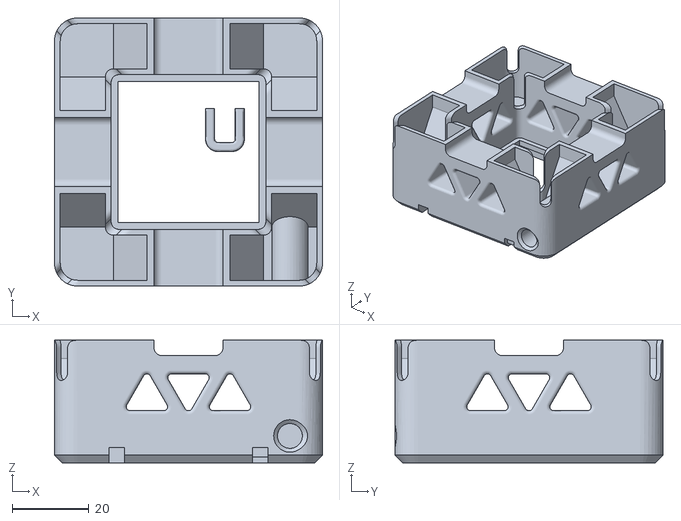
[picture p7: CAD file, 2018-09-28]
3D_print_files/v2.0/plates/Base_plate.stl
70.0 x 70.0 x 32.0

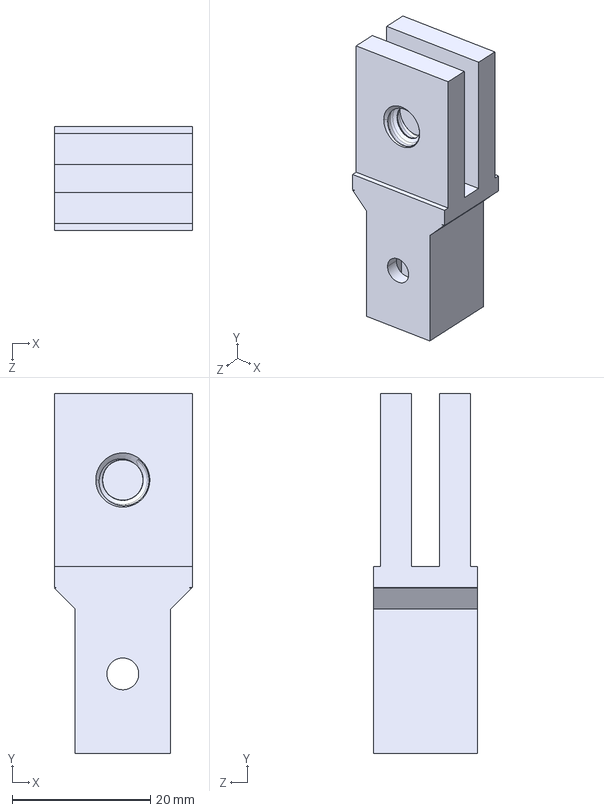
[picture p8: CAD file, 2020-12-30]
3D_print_files/v2.0/STEPs/Manipulator_Zaxis_v2.step
20.0 x 52.0 x 15.0 mm

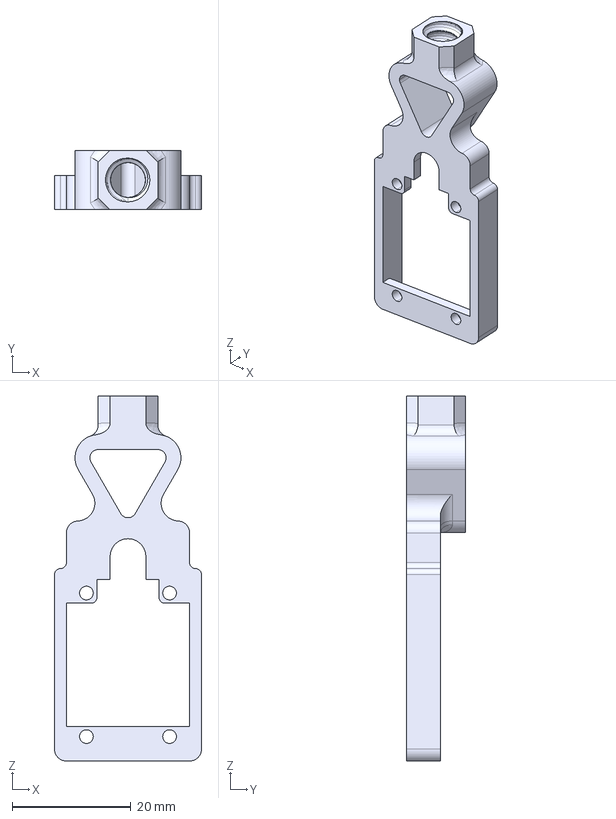
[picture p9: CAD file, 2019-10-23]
3D_print_files/v2.0/STEPs/sobianin/LED_holder/LED_holder_0.8.STEP
24.7 x 10.0 x 61.4 mm

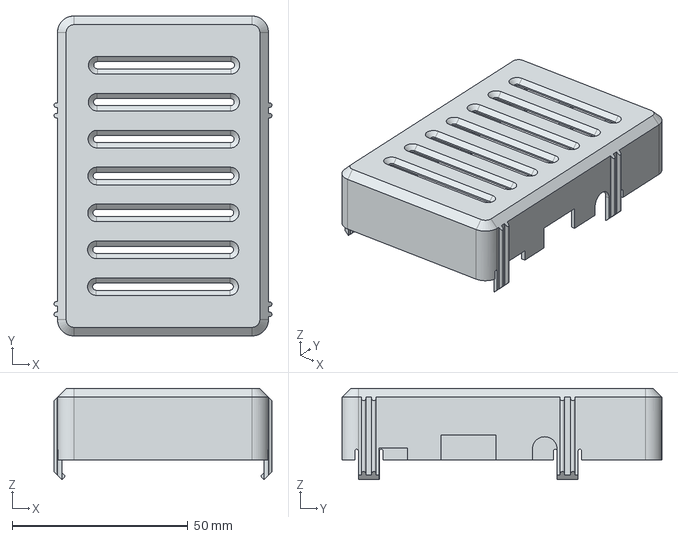
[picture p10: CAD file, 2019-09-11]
3D_print_files/v2.0/STEPs/sobianin/RaspberryCase_Top_v2.stp
62.0 x 91.0 x 26.0 mm

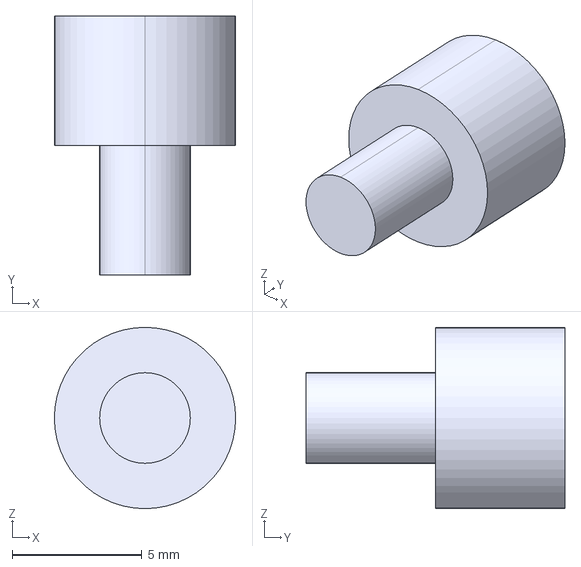
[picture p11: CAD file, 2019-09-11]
3D_print_files/v2.0/STEPs/sobianin/vise/dubel.STEP
7.00 x 10.0 x 7.00 mm

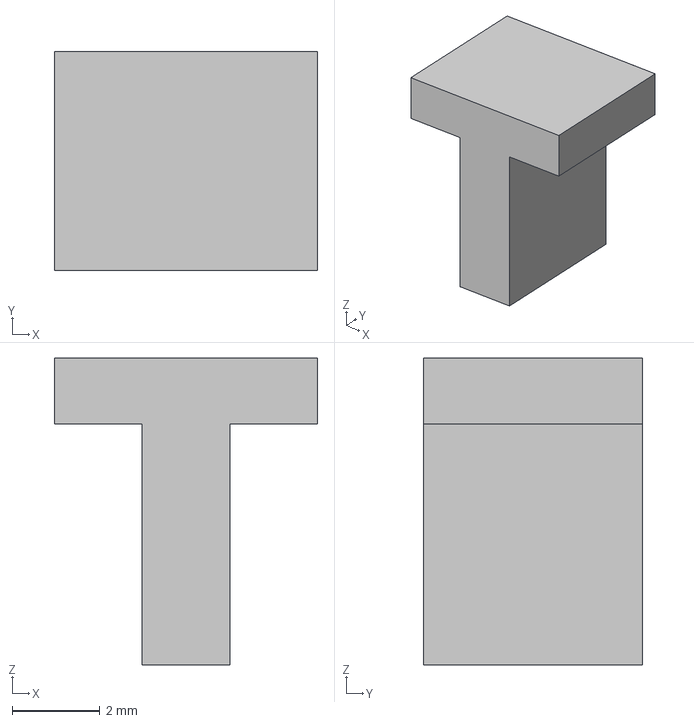
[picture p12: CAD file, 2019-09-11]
3D_print_files/v2.0/STEPs/sobianin/zaxis_T_holding_system/T-shaft.stp
6.00 x 5.00 x 7.00 mm

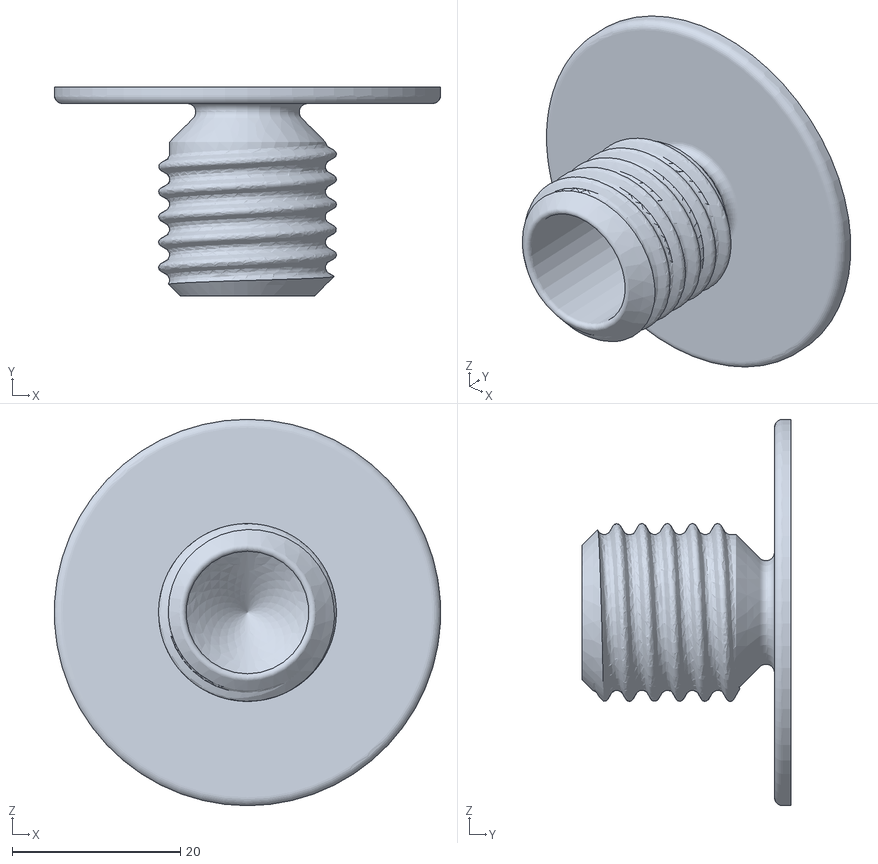
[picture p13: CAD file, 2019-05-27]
3D_print_files/v2.0/STLs/light_diffuser_print_in_white.stl
45.9 x 24.9 x 46.0

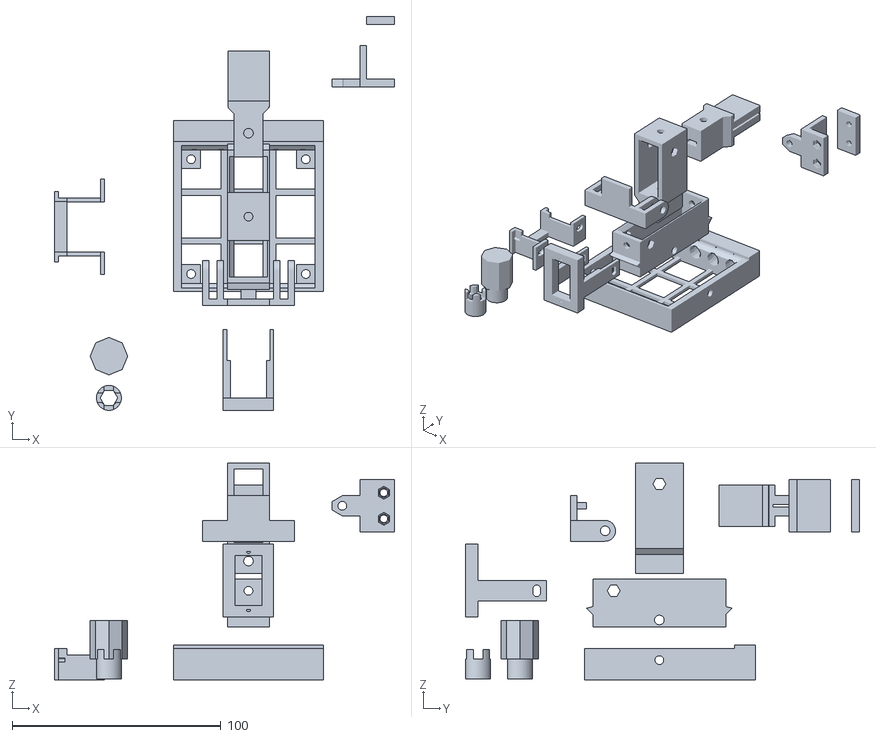
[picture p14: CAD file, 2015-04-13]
3D_print_files/Fly-Pi manipulator_v4.stl
163.0 x 189.0 x 104.0

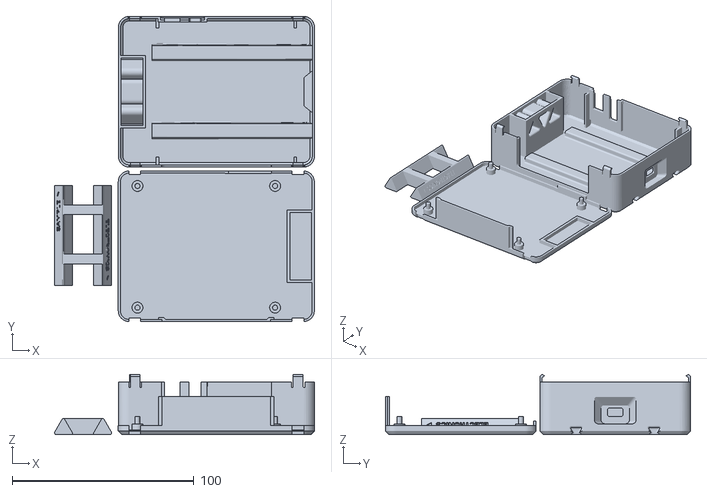
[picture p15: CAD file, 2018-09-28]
3D_print_files/v2.0/plates/PCB_case_plate.stl
143.2 x 168.1 x 33.2

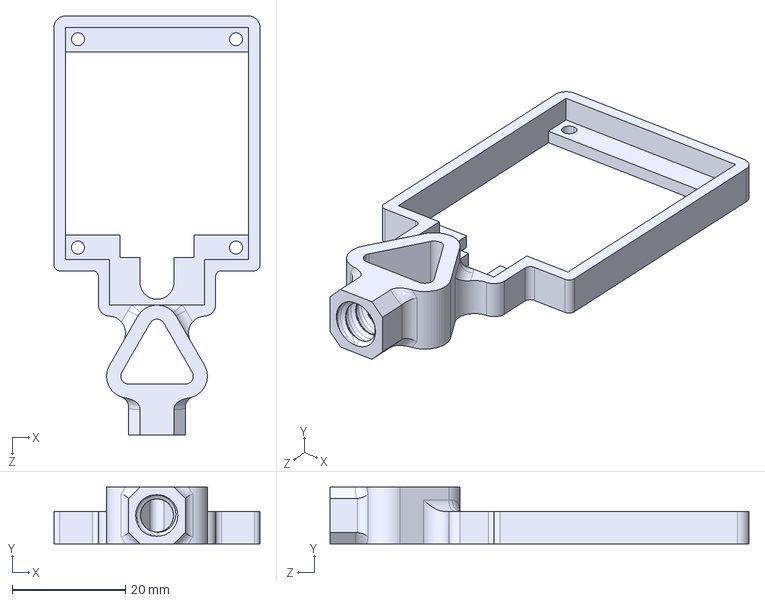
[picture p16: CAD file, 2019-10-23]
3D_print_files/v2.0/STEPs/sobianin/LED_holder/LED_holder_1.2_universal.STEP
36.4 x 10.0 x 74.1 mm

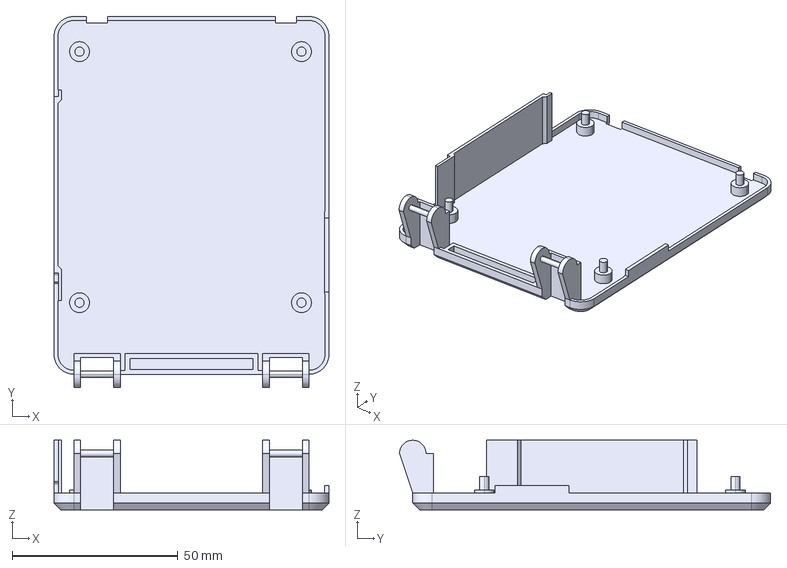
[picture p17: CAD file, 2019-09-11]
3D_print_files/v2.0/STEPs/sobianin/PCBCase_Bot_v2.STEP
83.0 x 112.0 x 21.0 mm

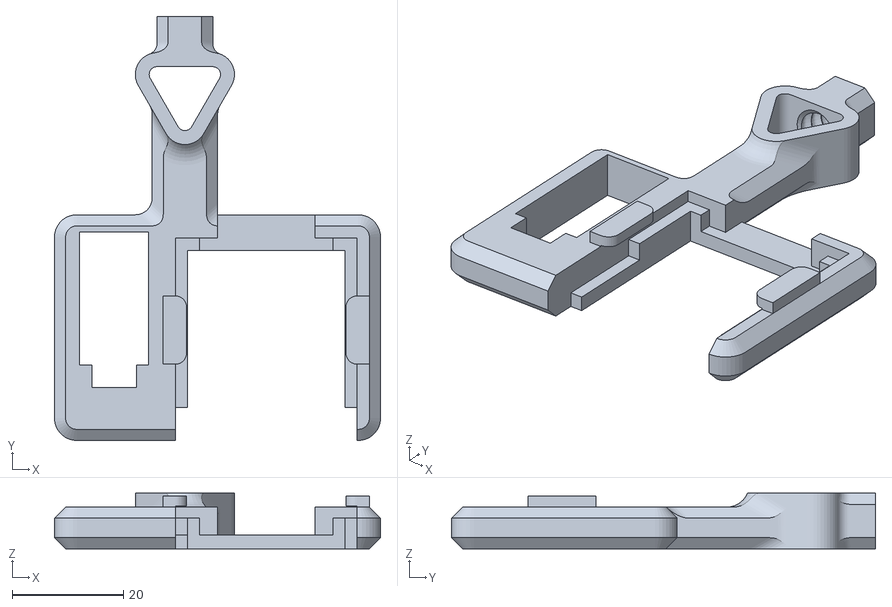
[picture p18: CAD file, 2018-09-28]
3D_print_files/v2.0/plates/ServoCameraMount.stl
58.5 x 76.1 x 10.00

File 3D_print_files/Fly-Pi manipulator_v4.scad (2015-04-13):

/// PARAMETERS FOR THE CUSTOMIZER

wall = 3;

X_range = 44; // Length(70) - B_X(20) - 2*wall(6) = 44
Y_range = 35; // Width(70) - C_Y(23) - 4*wall(12) = 38
Z_range = 15; // C_Topheight(40) - D_Z(12) - 2*Wall(6) = 22

Sliding_Gap = 0.1;

Separation_of_pieces = 20; // 

Radius_of_holes = 2.1;
Width_of_boat_slids = 7.4;
Height_of_boat_slids = 3.2;

///////////////////////// NOT FOR CUSTOMIZER BELOW HERE

module SEPARATION_OF_CUSTOMIZER_VARIABLES(){
}

sep = Separation_of_pieces; // seperation of pieces
gap = Sliding_Gap; // sliding space //

A_X = X_range+20+2*wall;
A_Y = Y_range+23+4*wall;
A_Z = 15; // 2 mm higher than before
A_Z_lower = 9.5;

A_extrawall = 1; // extra thickness of bottom layer walls
A_beams_Z = 2; // height of support beams

R_main = Radius_of_holes;
R_main_extra = 0.2; // extra radius for non-guiding holes
R_main_head = 4; // radius of screw head for part C
R_knob_in = 4.2; // Radius of Hex boats // M4

R_hex_small = 3.1;// Radius of Hex boats /7 M3
R_screw_small = 1.8; 
R_screw_mini = 1; 
Boatslot_small_height = 3;


Boatslot_width = Width_of_boat_slids; // how wide so that an M4 doesnt rotate?
Boatslot_height = Height_of_boat_slids; // how thick is an M4 boat?


////////////////////////////
//// BOTTOM PART (A)	///////
////////////////////////////
Cam_link = 10;

A_Base_Z = 19;
Airhole_R = 6;
Airhole_R2 = 4;
Airhole_spacing = 13;
Groud_clearance = ((A_Base_Z - Airhole_R*2)/2)/2;


module A_base(){
	translate([0,0,-A_Z_lower])cube([A_X+A_extrawall*2,A_Y+A_extrawall*2,A_Z], center = true);
	translate([0,A_Y/2+A_extrawall+Cam_link/2,-A_Z_lower+Groud_clearance/2])cube([A_X+A_extrawall*2,Cam_link,A_Z+Groud_clearance], center = true);
//translate([-Airhole_spacing,A_Y/2+A_extrawall+Cam_link/2,-A_Z_lower])cube([Cam_link,Cam_link,A_Z], center = true);
}



	

module A_basehole(){
	translate([0,0,-A_Z_lower])cube([A_X-wall*2,A_Y-wall*2,A_Z], center = true);
	translate([0,0,A_Z-13-A_Z_lower]){rotate ([90,0,90]) {cylinder($fn = 50, r = R_main, h = A_X+1+2*A_extrawall, center = true);}} // hole
	translate([0,A_Y/2-wall,A_Z/2-A_Z_lower]){rotate ([90,-15,90]){cylinder($fn = 3, r = wall, h = A_X-2*wall, center = true);}} // slope1
	translate([0,-A_Y/2+wall,A_Z/2-A_Z_lower]){rotate ([90,195,90]){cylinder($fn = 3, r = wall, h = A_X-2*wall, center = true);}} // slope2

	translate([-A_X/2+wall-Boatslot_small_height/2,-M_axis_offset+M_width/2+2*M_wall,A_Z-13-A_Z_lower]){
		rotate ([90,0,90]) {cylinder($fn = 6, r = R_hex_small, h = Boatslot_small_height, center = true);}} // screwholeHex3
	translate([-A_X/2+wall-Boatslot_small_height/2,-M_axis_offset-M_width/2-2*M_wall,A_Z-13-A_Z_lower]){
		rotate ([90,0,90]) {cylinder($fn = 6, r = R_hex_small, h = Boatslot_small_height, center = true);}} // screwholeHex4
	translate([-A_X/2+wall/2,-M_axis_offset+M_width/2+2*M_wall,A_Z-13-A_Z_lower]){
		rotate ([90,0,90]) {cylinder($fn = 50, r = R_screw_small, h = 2*wall, center = true);}} // screwhole3
	translate([-A_X/2+wall/2,-M_axis_offset-M_width/2-2*M_wall,A_Z-13-A_Z_lower]){
		rotate ([90,0,90]) {cylinder($fn = 50, r = R_screw_small, h = 2*wall, center = true);}} // screwhole4

	translate([-Airhole_spacing*2,A_Y/2+A_extrawall+Cam_link/2,-A_Base_Z/2+Groud_clearance]){rotate ([90,90,0]) {cylinder(r = Airhole_R, h = Cam_link, center = true );}} // BigLink hole1	
	translate([-Airhole_spacing,A_Y/2+A_extrawall+Cam_link/2,-A_Base_Z/2+Groud_clearance]){rotate ([90,90,0]) {cylinder(r = Airhole_R, h = Cam_link, center = true );}} // BigLink hole2
	translate([0,A_Y/2+A_extrawall+Cam_link/2,-A_Base_Z/2+Groud_clearance]){rotate ([90,90,0]) {cylinder(r = Airhole_R, h = Cam_link, center = true );}} // BigLink hole3
	translate([Airhole_spacing,A_Y/2+A_extrawall+Cam_link/2,-A_Base_Z/2+Groud_clearance]){rotate ([90,90,0]) {cylinder(r = Airhole_R, h = Cam_link, center = true );}} // BigLink hole4
	translate([Airhole_spacing*2,A_Y/2+A_extrawall+Cam_link/2,-A_Base_Z/2+Groud_clearance]){rotate ([90,90,0]) {cylinder(r = Airhole_R, h = Cam_link, center = true );}} // BigLink hole5
	
	translate([-Airhole_spacing*2,A_Y/2+A_extrawall+Cam_link/2,-A_Base_Z/2+Groud_clearance]){rotate ([90,90,0]) {cylinder(r = Airhole_R2, h = Cam_link*2, center = true );}} // BigLink hole1	
	translate([-Airhole_spacing,A_Y/2+A_extrawall+Cam_link/2,-A_Base_Z/2+Groud_clearance]){rotate ([90,90,0]) {cylinder(r = Airhole_R2, h = Cam_link*2, center = true );}} // BigLink hole2
	translate([0,A_Y/2+A_extrawall+Cam_link/2,-A_Base_Z/2+Groud_clearance]){rotate ([90,90,0]) {cylinder(r = Airhole_R2, h = Cam_link*2, center = true );}} // BigLink hole3
	translate([Airhole_spacing,A_Y/2+A_extrawall+Cam_link/2,-A_Base_Z/2+Groud_clearance]){rotate ([90,90,0]) {cylinder(r = Airhole_R2, h = Cam_link*2, center = true );}} // BigLink hole4
	translate([Airhole_spacing*2,A_Y/2+A_extrawall+Cam_link/2,-A_Base_Z/2+Groud_clearance]){rotate ([90,90,0]) {cylinder(r = Airhole_R2, h = Cam_link*2, center = true );}} // BigLink hole5



}
module A_base_beams(){
	translate([0,A_Y/6,-A_Z/2+A_beams_Z/2-A_Z_lower]){cube([A_X,wall,A_beams_Z], center = true);}
	translate([0,-A_Y/6,-A_Z/2+A_beams_Z/2-A_Z_lower]){cube([A_X,wall,A_beams_Z], center = true);}
	translate([A_X/6,0,-A_Z/2+A_beams_Z/2-A_Z_lower]){cube([wall,A_Y,A_beams_Z], center = true);}
	translate([-A_X/6,0,-A_Z/2+A_beams_Z/2-A_Z_lower]){cube([wall,A_Y,A_beams_Z], center = true);}
	translate([A_X/2-wall*2.5,A_Y/2-wall*2.5,-A_Z/2-A_Z_lower+A_beams_Z/2]){cube([wall*3,wall*3,A_beams_Z], center = true);} // corner1
	translate([-A_X/2+wall*2.5,A_Y/2-wall*2.5,-A_Z/2-A_Z_lower+A_beams_Z/2]){cube([wall*3,wall*3,A_beams_Z], center = true);} // corner2
	translate([A_X/2-wall*2.5,-A_Y/2+wall*2.5,-A_Z/2-A_Z_lower+A_beams_Z/2]){cube([wall*3,wall*3,A_beams_Z], center = true);} // corner3
	translate([-A_X/2+wall*2.5,-A_Y/2+wall*2.5,-A_Z/2-A_Z_lower+A_beams_Z/2]){cube([wall*3,wall*3,A_beams_Z], center = true);} // corner4


}
module A_base_beams_holes(){
	translate([A_X/2-wall*2.5,A_Y/2-wall*2.5,-A_Z/2-A_Z_lower+A_beams_Z/2]){cylinder($fn = 50, r = R_main, h = A_beams_Z+1, center = true);} // cornerhole1
	translate([-A_X/2+wall*2.5,A_Y/2-wall*2.5,-A_Z/2-A_Z_lower+A_beams_Z/2]){cylinder($fn = 50, r = R_main, h = A_beams_Z+1, center = true);} // cornerhole2
	translate([A_X/2-wall*2.5,-A_Y/2+wall*2.5,-A_Z/2-A_Z_lower+A_beams_Z/2]){cylinder($fn = 50, r = R_main, h = A_beams_Z+1, center = true);} // cornerhole3
	translate([-A_X/2+wall*2.5,-A_Y/2+wall*2.5,-A_Z/2-A_Z_lower+A_beams_Z/2]){cylinder($fn = 50, r = R_main, h = A_beams_Z+1, center = true);} // cornerhole4
}
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

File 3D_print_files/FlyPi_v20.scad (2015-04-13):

/// ///
/// LARVAL BEHAVIOUR SETUP v1; 2014 08 21 ///
/// by Tom Baden (thingyverse ID: tbaden) ///
/// thomas.baden@uni-tuebingen.de ///
/// tombaden.wordpress.com ///
/// ///

/////////////////////////////////////////////////////////////////////////////////


sep = 30;

/////////////////// BASE
Walls = 5;
Borders = 15;
Walls_thinning = 4;
Tol = 0.2;

P_XY = 40+1;
P_Z = 3;
P_border = 12;
P_ridge = 2;
P_cable = 3;
T_cableZ = 4;
T_cableY = 12;
T_cable_offset = 8;
MarkerLED_R = 3+Tol;
MarkerLED_Z = 2; // depth beneath surface
MarkerLED_XY = 4; //viewhole size

Sidestand = 50;
Sidestand_thickness = Walls;

RPi_Width = 56+Walls*2;
RPi_groundZ = 17; // 65; for RPi B (not plus)
RPi_holedist_Y = 49/2; // 15.5; // for RPi B (not plus)
RPi_holedist_Yb = 49/2; //-10; // for RPi B (not plus)
RPi_holedist_Z = 58; //54.5; // for RPi B (not plus)

Cam_X = 32.2;//24;
Cam_Y = 32.2;//25;
Cam_X_offset = 0;// 2.5;
C_Z = 2;
C_Z2 = 5;
C_ridge = 2;
Cam_Zfloat = 200;
CamGroove_X = 12;
CamGroove_Y = 16;
CamGroove2_Y = 24;

Tube_wall = 1.5;

S_hole_R = 1.7;
S_mount_R = 4;

Mount_h = 19;

A_Base_X = P_XY+P_border*2 + Walls + Sidestand;
A_Base_Y = RPi_Width;
A_Base_Z = 19;

A_Wall_X = Walls;
A_Wall_Y = A_Base_Y;
A_Wall_Y_long = 10;
A_Wall_Z = RPi_groundZ+RPi_holedist_Z+25;
A_Wall_Z_long = Cam_Zfloat+Walls;
A_extramount_Z = 100;

Stabiliser_R = 12;
Airhole_R = 6;
Airhole_spacing = 13;


A1_screw_R = 1.5;
A1_offset = 3;


module A(){
	translate([-A_Base_X/2+P_XY/2+P_border,0,-A_Base_Z/2]){cube([A_Base_X,A_Base_Y,A_Base_Z], center = true );} // BASE
	translate([-P_XY/2-P_border-Walls/2,A_Base_Y/2-Walls+Tol/2,0]){rotate ([90,0,0]) {cylinder($fn = 50, r = Stabiliser_R, h = Walls*2-Tol, center = true );}} // Support1	
	translate([-P_XY/2-P_border-Walls/2,-A_Base_Y/2+Walls-Tol/2,0]){rotate ([90,0,0]) {cylinder($fn = 50, r = Stabiliser_R, h = Walls*2-Tol, center = true );}} // Support2	


//	translate([0,-A_Base_Y/2+A_Wall_X/2,A_extramount_Z/2]){cube([A_Wall_Y_long,A_Wall_X,A_extramount_Z], center = true );} // low_mount
//	translate([0,-A_Base_Y/2+A_Wall_X/2,0]){rotate ([0,270,90]) {cylinder($fn = 3, r = A_Wall_Y/2, h = Walls, center = true );}} // WALL_roun
}

module A_sub(){
	translate([0,0,-P_Z/2]){cube([P_XY+2*Tol,P_XY+2*Tol,P_Z], center = true );} // Peltier groove
	translate([-A_Base_Y/4,(P_XY+2*Tol)/2-(P_cable+2*Tol)/2,-P_Z/2]){cube([A_Base_Y,P_cable+2*Tol,P_Z], center = true );} // Peltier cable1
	translate([-A_Base_Y/4,-(P_XY+2*Tol)/2+(P_cable+2*Tol)/2,-P_Z/2]){cube([A_Base_Y,P_cable+2*Tol,P_Z], center = true );} // Peltier cable1
	translate([-A_Base_Y/2,0,-MarkerLED_R-MarkerLED_Z]){rotate ([0,90,0]) {cylinder($fn = 50, r = MarkerLED_R, h = A_Base_Y, center = true );}} // MarkerLed HOLE
	translate([-P_XY/2-MarkerLED_XY/2-1,0,-MarkerLED_Z]){cube([MarkerLED_XY,MarkerLED_XY,2*MarkerLED_Z], center = true );} // MarkerLed opening
	

//MarkerLED_YZ

	translate([0,0,-A_Base_Z/2]){cube([P_XY-P_ridge*2,P_XY-P_ridge*2,A_Base_Z], center = true );} // Peltier below
	translate([-A_Base_X/2-Walls,0,-A_Base_Z/2]){cube([Sidestand-Walls*3,A_Base_Y-Walls*2,A_Base_Z], center = true );} // Sidestand Hole
	translate([-A_Base_X/2-Walls/2-Walls,0,-A_Base_Z/2+Sidestand_thickness]){cube([Sidestand-Walls*2,A_Base_Y,A_Base_Z], center = true );} // Sidestand Hole shallow
	translate([-P_XY/2-P_border-Walls/2,0,-A_Base_Z/2]){cube([Walls+Tol*2,A_Base_Y-Walls*4,A_Base_Z], center = true );} // Wall_linkhole
	translate([-P_XY/2-P_border-A_Wall_X/2,0,A_Wall_Z/2]){cube([A_Wall_X+Tol*2,A_Wall_Y,A_Wall_Z], center = true );} // Sidestand_slot
	translate([Airhole_spacing,0,-A_Base_Z/2]){rotate ([90,90,0]) {cylinder(r = Airhole_R, h = A_Base_Y, center = true );}} // Air holes
	translate([0,0,-A_Base_Z/2]){rotate ([90,90,0]) {cylinder(r = Airhole_R, h = A_Base_Y, center = true );}} // Air holes
	translate([-Airhole_spacing,0,-A_Base_Z/2]){rotate ([90,90,0]) {cylinder(r = Airhole_R, h = A_Base_Y, center = true );}} // Air holes
	translate([+A_Base_Y/2,0,-A_Base_Z/2]){rotate ([0,90,0]) {cylinder(r = Airhole_R, h = A_Base_Y, center = true );}} // Air holes
	translate([0,-Airhole_spacing,-A_Base_Z/2]){rotate ([0,90,0]) {cylinder(r = Airhole_R, h = A_Base_Y, center = true );}} // Air holes
	translate([0,Airhole_spacing,-A_Base_Z/2]){rotate ([0,90,0]) {cylinder(r = Airhole_R, h = A_Base_Y, center = true );}} // Air holes

// screwholes
	translate([-(P_XY/2-A1_offset),P_XY/2+A1_offset,-Walls]){rotate ([0,0,0]) {cylinder($fn=20, r = A1_screw_R, h = Walls*2, center = true );}} // screwhole
	translate([-(P_XY/2-A1_offset),-(P_XY/2+A1_offset),-Walls]){rotate ([0,0,0]) {cylinder($fn=20,r = A1_screw_R, h = Walls*2, center = true );}} // screwhole
	translate([(P_XY/2-A1_offset),P_XY/2+A1_offset,-Walls]){rotate ([0,0,0]) {cylinder($fn=20,r = A1_screw_R, h = Walls*2, center = true );}} // screwhole
	translate([(P_XY/2-A1_offset),-(P_XY/2+A1_offset),-Walls]){rotate ([0,0,0]) {cylinder($fn=20,r = A1_screw_R, h = Walls*2, center = true );}} // screwhole
}

difference(){A();A_sub();}

//// Module A1 - thermistor holder


module A1(){
	translate([P_XY/2-A1_offset,P_XY/2+A1_offset,Walls*2]){cube([A1_offset*2,A1_offset*5,Walls/3], center = true );} // clamp
	translate([P_XY/2-A1_offset,P_XY/2+A1_offset*3,Walls*2-Walls/3]){cube([A1_offset*2,A1_offset,Walls/3], center = true );} // clamp
	translate([P_XY/2-A1_offset,-P_XY/2-A1_offset,Walls*2]){cube([A1_offset*2,A1_offset*5,Walls/3], center = true );} // clamp
	translate([P_XY/2-A1_offset,-P_XY/2-A1_offset*3,Walls*2-Walls/3]){cube([A1_offset*2,A1_offset,Walls/3], center = true );} // clamp
	translate([-P_XY/2+A1_offset,-P_XY/2-A1_offset,Walls*2]){cube([A1_offset*2,A1_offset*5,Walls/3], center = true );} // clamp
	translate([-P_XY/2+A1_offset,-P_XY/2-A1_offset*3,Walls*2-Walls/3]){cube([A1_offset*2,A1_offset,Walls/3], center = true );} // clamp

   translate([-P_XY/2+A1_offset,P_XY/2+A1_offset/4,Walls*2]){cube([A1_offset*2,A1_offset*6.5,Walls/3], center = true );} // Thermistor clamp
	translate([-P_XY/2+A1_offset,P_XY/2+A1_offset*3,7]){cube([A1_offset*2,A1_offset,5], center = true );} // Thermistor clamp footbig

	//translate([-P_XY/2+A1_offset,P_XY/2-A1_offset*1,Walls*2-Walls/3]){cube([A1_offset*2,A1_offset,Walls/3], center = true );} // clamp
	translate([-P_XY/2+A1_offset,P_XY/2-A1_offset*2.5,Walls*2-Walls/3]){cube([A1_offset*2,A1_offset,Walls/3], center = true );} // clamp

}

module A1_sub(){
	translate([-(P_XY/2-A1_offset),P_XY/2+A1_offset,Walls*2]){rotate ([0,0,0]) {cylinder($fn=20,r = A1_screw_R, h = Walls/2, center = true );}} // screwhole
	translate([-(P_XY/2-A1_offset),-(P_XY/2+A1_offset),Walls*2]){rotate ([0,0,0]) {cylinder($fn=20,r = A1_screw_R, h = Walls/2, center = true );}} // screwhole
	translate([(P_XY/2-A1_offset),P_XY/2+A1_offset,Walls*2]){rotate ([0,0,0]) {cylinder($fn=20,r = A1_screw_R, h = Walls/2, center = true );}} // screwhole
	translate([(P_XY/2-A1_offset),-(P_XY/2+A1_offset),Walls*2]){rotate ([0,0,0]) {cylinder($fn=20,r = A1_screw_R, h = Walls/2, center = true );}} // screwhole
}

difference(){A1();A1_sub();}

///// MODULE B - WALL

module B(){
	translate([-P_XY/2-P_border-A_Wall_X/2,0,A_Wall_Z/2+sep]){cube([A_Wall_X,A_Wall_Y,A_Wall_Z], center = true );} // WALL
	translate([-P_XY/2-P_border-A_Wall_X/2,0,A_Wall_Z_long/2+sep]){cube([A_Wall_X,A_Wall_Y_long,A_Wall_Z_long], center = true );} // WALL_extra
	translate([-P_XY/2-P_border-A_Wall_X/2,0,0.5+sep-A_Base_Z/2]){cube([Walls,A_Base_Y-Walls*4-Tol*2,A_Base_Z], center = true );} // WALL_link
	translate([-P_XY/2-P_border-A_Wall_X/2,0,A_Wall_Z+sep-A_Wall_Y/999]){rotate ([0,270,0]) {cylinder($fn = 3, r = A_Wall_Y/2, h = Walls, center = true );}} // WALL_rounding top
	//translate([-P_XY/2-P_border-A_Wall_X/2,0,A_Wall_Z+sep+A_Wall_Y/2-A_Wall_Y/8]){rotate ([0,270,0]) {cylinder($fn = 3, r = A_Wall_Y/4, h = Walls, center = true );}} // WALL_rounding top

	
}
module B2(){
	translate([-P_XY/2-P_border+1.7*Walls-Mount_h,RPi_holedist_Yb,RPi_groundZ+sep]){rotate ([0,90,0]) {cylinder(r = S_mount_R, h = Mount_h, center = true );}} // m hole_bottom
	translate([-P_XY/2-P_border+1.7*Walls-Mount_h,RPi_holedist_Y,RPi_groundZ+RPi_holedist_Z+sep]){rotate ([0,90,0]) {cylinder(r = S_mount_R, h = Mount_h, center = true );}} // m hole_top
	translate([-P_XY/2-P_border+1.7*Walls-Mount_h,-RPi_holedist_Yb,RPi_groundZ+sep]){rotate ([0,90,0]) {cylinder(r = S_mount_R, h = Mount_h, center = true );}} // m hole_bottom
	translate([-P_XY/2-P_border+1.7*Walls-Mount_h,-RPi_holedist_Y,RPi_groundZ+RPi_holedist_Z+sep]){rotate ([0,90,0]) {cylinder(r = S_mount_R, h = Mount_h, center = true );}} // m hole_top
}
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

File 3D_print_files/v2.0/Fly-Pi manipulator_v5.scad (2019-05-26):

/// PARAMETERS FOR THE CUSTOMIZER

wall = 3;

X_range = 44; // Length(70) - B_X(20) - 2*wall(6) = 44
Y_range = 35; // Width(70) - C_Y(23) - 4*wall(12) = 38
Z_range = 30; // C_Topheight(40) - D_Z(12) - 2*Wall(6) = 22


Sliding_Gap = 0.1;


Separation_of_pieces = 20; // 

Radius_of_holes = 2.1;
Width_of_boat_slids = 7.4;
Height_of_boat_slids = 3.2;


AFlag=0;
BFlag=1;

CFlag=0;
DFlag=0;
EFlag=0;
E1Flag=0;
KFlag=0;
K1Flag=0;
MFlag=0;
M1Flag=0;

///////////////////////// NOT FOR CUSTOMIZER BELOW HERE

module SEPARATION_OF_CUSTOMIZER_VARIABLES(){
}

sep = Separation_of_pieces; // seperation of pieces
gap = Sliding_Gap; // sliding space //

A_X = X_range+20+2*wall;
A_Y = Y_range+23+4*wall;
A_Z = 15; // 2 mm higher than before
A_Z_lower = 9.5;

A_extrawall = 1; // extra thickness of bottom layer walls
A_beams_Z = 2; // height of support beams

R_main = Radius_of_holes;
R_main_extra = 0.2; // extra radius for non-guiding holes
R_main_head = 4; // radius of screw head for part C
R_knob_in = 4.2; // Radius of Hex boats // M4

R_hex_small = 3.1;// Radius of Hex boats /7 M3
R_screw_small = 1.8; 
R_screw_mini = 1; 
Boatslot_small_height = 3;


Boatslot_width = Width_of_boat_slids; // how wide so that an M4 doesnt rotate?
Boatslot_height = Height_of_boat_slids; // how thick is an M4 boat?


////////////////////////////
//// BOTTOM PART (A)	///////
////////////////////////////
Cam_link = 10;

A_Base_Z = 19;
Airhole_R = 6;
Airhole_R2 = 4;
Airhole_spacing = 13;
Groud_clearance = ((A_Base_Z - Airhole_R*2)/2)/2;


module A_base(){
	translate([0,0,-A_Z_lower])cube([A_X+A_extrawall*2,A_Y+A_extrawall*2,A_Z], center = true);
	translate([0,A_Y/2+A_extrawall+Cam_link/2,-A_Z_lower+Groud_clearance/2])cube([A_X+A_extrawall*2,Cam_link,A_Z+Groud_clearance], center = true);
//translate([-Airhole_spacing,A_Y/2+A_extrawall+Cam_link/2,-A_Z_lower])cube([Cam_link,Cam_link,A_Z], center = true);
}



	

module A_basehole(){
	translate([0,0,-A_Z_lower])cube([A_X-wall*2,A_Y-wall*2,A_Z], center = true);
	translate([0,0,A_Z-13-A_Z_lower]){rotate ([90,0,90]) {cylinder($fn = 50, r = R_main, h = A_X+1+2*A_extrawall, center = true);}} // hole
	translate([0,A_Y/2-wall,A_Z/2-A_Z_lower]){rotate ([90,-15,90]){cylinder($fn = 3, r = wall, h = A_X-2*wall, center = true);}} // slope1
	translate([0,-A_Y/2+wall,A_Z/2-A_Z_lower]){rotate ([90,195,90]){cylinder($fn = 3, r = wall, h = A_X-2*wall, center = true);}} // slope2

	translate([-A_X/2+wall-Boatslot_small_height/2,-M_axis_offset+M_width/2+2*M_wall,A_Z-13-A_Z_lower]){
		rotate ([90,0,90]) {cylinder($fn = 6, r = R_hex_small, h = Boatslot_small_height, center = true);}} // screwholeHex3
	translate([-A_X/2+wall-Boatslot_small_height/2,-M_axis_offset-M_width/2-2*M_wall,A_Z-13-A_Z_lower]){
		rotate ([90,0,90]) {cylinder($fn = 6, r = R_hex_small, h = Boatslot_small_height, center = true);}} // screwholeHex4
	translate([-A_X/2+wall/2,-M_axis_offset+M_width/2+2*M_wall,A_Z-13-A_Z_lower]){
		rotate ([90,0,90]) {cylinder($fn = 50, r = R_screw_small, h = 2*wall, center = true);}} // screwhole3
	translate([-A_X/2+wall/2,-M_axis_offset-M_width/2-2*M_wall,A_Z-13-A_Z_lower]){
		rotate ([90,0,90]) {cylinder($fn = 50, r = R_screw_small, h = 2*wall, center = true);}} // screwhole4

	translate([-Airhole_spacing*2,A_Y/2+A_extrawall+Cam_link/2,-A_Base_Z/2+Groud_clearance]){rotate ([90,90,0]) {cylinder(r = Airhole_R, h = Cam_link, center = true );}} // BigLink hole1	
	translate([-Airhole_spacing,A_Y/2+A_extrawall+Cam_link/2,-A_Base_Z/2+Groud_clearance]){rotate ([90,90,0]) {cylinder(r = Airhole_R, h = Cam_link, center = true );}} // BigLink hole2
	translate([0,A_Y/2+A_extrawall+Cam_link/2,-A_Base_Z/2+Groud_clearance]){rotate ([90,90,0]) {cylinder(r = Airhole_R, h = Cam_link, center = true );}} // BigLink hole3
	translate([Airhole_spacing,A_Y/2+A_extrawall+Cam_link/2,-A_Base_Z/2+Groud_clearance]){rotate ([90,90,0]) {cylinder(r = Airhole_R, h = Cam_link, center = true );}} // BigLink hole4
	translate([Airhole_spacing*2,A_Y/2+A_extrawall+Cam_link/2,-A_Base_Z/2+Groud_clearance]){rotate ([90,90,0]) {cylinder(r = Airhole_R, h = Cam_link, center = true );}} // BigLink hole5
	
	translate([-Airhole_spacing*2,A_Y/2+A_extrawall+Cam_link/2,-A_Base_Z/2+Groud_clearance]){rotate ([90,90,0]) {cylinder(r = Airhole_R2, h = Cam_link*2, center = true );}} // BigLink hole1	
	translate([-Airhole_spacing,A_Y/2+A_extrawall+Cam_link/2,-A_Base_Z/2+Groud_clearance]){rotate ([90,90,0]) {cylinder(r = Airhole_R2, h = Cam_link*2, center = true );}} // BigLink hole2
	translate([0,A_Y/2+A_extrawall+Cam_link/2,-A_Base_Z/2+Groud_clearance]){rotate ([90,90,0]) {cylinder(r = Airhole_R2, h = Cam_link*2, center = true );}} // BigLink hole3
	translate([Airhole_spacing,A_Y/2+A_extrawall+Cam_link/2,-A_Base_Z/2+Groud_clearance]){rotate ([90,90,0]) {cylinder(r = Airhole_R2, h = Cam_link*2, center = true );}} // BigLink hole4
	translate([Airhole_spacing*2,A_Y/2+A_extrawall+Cam_link/2,-A_Base_Z/2+Groud_clearance]){rotate ([90,90,0]) {cylinder(r = Airhole_R2, h = Cam_link*2, center = true );}} // BigLink hole5



}
module A_base_beams(){
	translate([0,A_Y/6,-A_Z/2+A_beams_Z/2-A_Z_lower]){cube([A_X,wall,A_beams_Z], center = true);}
	translate([0,-A_Y/6,-A_Z/2+A_beams_Z/2-A_Z_lower]){cube([A_X,wall,A_beams_Z], center = true);}
	translate([A_X/6,0,-A_Z/2+A_beams_Z/2-A_Z_lower]){cube([wall,A_Y,A_beams_Z], center = true);}
	translate([-A_X/6,0,-A_Z/2+A_beams_Z/2-A_Z_lower]){cube([wall,A_Y,A_beams_Z], center = true);}
	translate([A_X/2-wall*2.5,A_Y/2-wall*2.5,-A_Z/2-A_Z_lower+A_beams_Z/2]){cube([wall*3,wall*3,A_beams_Z], center = true);} // corner1
	translate([-A_X/2+wall*2.5,A_Y/2-wall*2.5,-A_Z/2-A_Z_lower+A_beams_Z/2]){cube([wall*3,wall*3,A_beams_Z], center = true);} // corner2
	translate([A_X/2-wall*2.5,-A_Y/2+wall*2.5,-A_Z/2-A_Z_lower+A_beams_Z/2]){cube([wall*3,wall*3,A_beams_Z], center = true);} // corner3
	translate([-A_X/2+wall*2.5,-A_Y/2+wall*2.5,-A_Z/2-A_Z_lower+A_beams_Z/2]){cube([wall*3,wall*3,A_beams_Z], center = true);} // corner4


}
module A_base_beams_holes(){
	translate([A_X/2-wall*2.5,A_Y/2-wall*2.5,-A_Z/2-A_Z_lower+A_beams_Z/2]){cylinder($fn = 50, r = R_main, h = A_beams_Z+1, center = true);} // cornerhole1
	translate([-A_X/2+wall*2.5,A_Y/2-wall*2.5,-A_Z/2-A_Z_lower+A_beams_Z/2]){cylinder($fn = 50, r = R_main, h = A_beams_Z+1, center = true);} // cornerhole2
	translate([A_X/2-wall*2.5,-A_Y/2+wall*2.5,-A_Z/2-A_Z_lower+A_beams_Z/2]){cylinder($fn = 50, r = R_main, h = A_beams_Z+1, center = true);} // cornerhole3
	translate([-A_X/2+wall*2.5,-A_Y/2+wall*2.5,-A_Z/2-A_Z_lower+A_beams_Z/2]){cylinder($fn = 50, r = R_main, h = A_beams_Z+1, center = true);} // cornerhole4
}

if (AFlag==1){
difference(){A_base();A_basehole();}
difference(){A_base_beams();A_base_beams_holes();}
}
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

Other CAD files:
3D_print_files/v2.0/STEPs/RaspberryCase_Top_v2.step
3D_print_files/v2.0/STEPs/PCBCase_Bot_v2.step
3D_print_files/v2.0/STEPs/sobianin/LED_holder/LED_holder_rectangle_0.8.STEP
3D_print_files/v1.0/Fly-Pi manipulator_v5.scad
3D_print_files/v1.0/Fly-Pi manipulator_v5.stl
3D_print_files/v1.0/FlyPi_v29.stl
3D_print_files/v1.0/FlyPi_v29_cam_holder.stl
3D_print_files/v1.0/FlyPi_v29_paper.scad
3D_print_files/v1.0/FlyPi_v30.scad
3D_print_files/v1.0/individual_stls/angled_stick.stl
3D_print_files/v1.0/individual_stls/base.stl
3D_print_files/v1.0/individual_stls/cam_mount.step
3D_print_files/v1.0/individual_stls/cam_mount.stl
3D_print_files/v1.0/individual_stls/cam_mount_waveshare.stl
3D_print_files/v1.0/individual_stls/diffusor.step
3D_print_files/v1.0/individual_stls/diffusor.stl
3D_print_files/v1.0/individual_stls/fluorescence1.step
3D_print_files/v1.0/individual_stls/fluorescence1.stl
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

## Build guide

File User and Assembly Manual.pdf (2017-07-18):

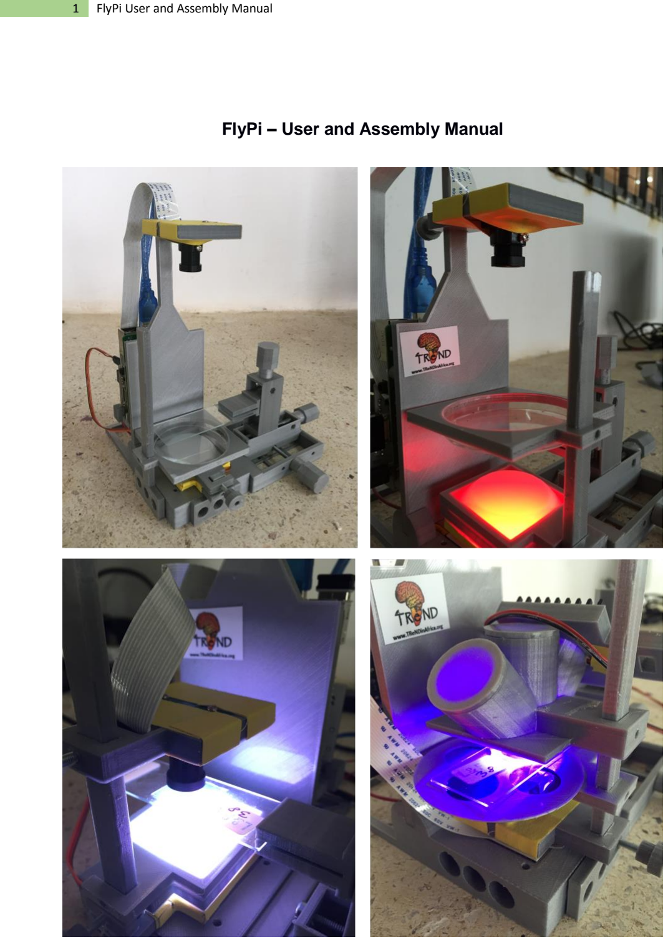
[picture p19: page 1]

1 FlyPi User and Assembly Manual

### FlyPi – User and Assembly Manual

## Index

Software
Here we describe two installation methods.

Method 1 should be used if:

1. If the user wants to know what is “under the hood”, which libraries are necessary, how to update the software in a GNU/Linux distribution, how to install packages and download repositories form GitHub.
2. If the user is located in a place where internet connectivity is always available (but not necessarily reliable as this method requires smaller downloads).
3. The FlyPi is to be used as a teaching tool for building your own lab equipment.

Method 2 should be used if:

1. The user does not mind what is under the hood, and also does not mind using a possibly outdated version of the system.
2. The user is going to use the system in a place where there is poor internet connectivity, and can download a single (large) image file beforehand.

Method 1 (full)
Installing the operating system (OS)
The OS used to develop is called Raspian, and can be installed using NOOBS (and https://www.raspberrypi.org/help/videos/#noobs-setup for an excellent video tutorial) or directly via the Raspian image (https://www.raspian.org/RaspianImages).

Enabling the Camera Module and serial communication
Once the OS has been installed, the camera module and the serial communication need to be enabled. This can be done by going to “Raspberry Pi configuration” and selecting the check-boxes as indicated.

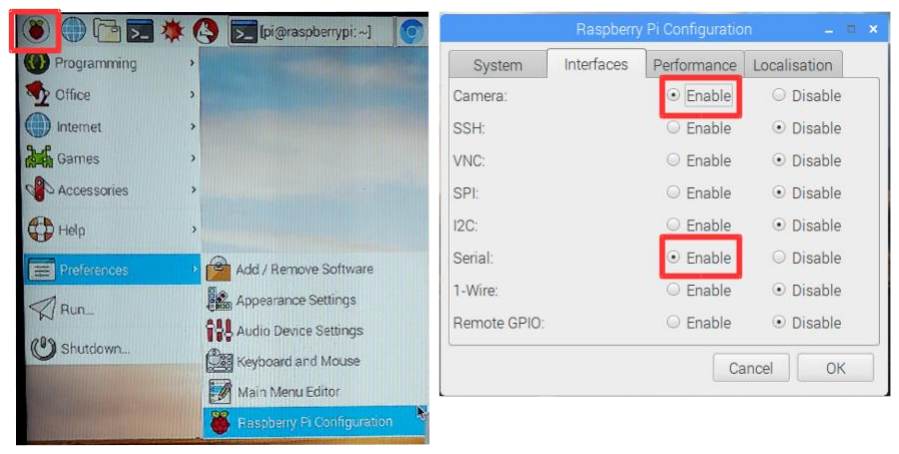
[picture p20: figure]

Running a terminal and installing software on GNU/Linux systems
Installing software on GNU/Linux distributions (as the one used on the Raspberry Pi), is easily done using a command terminal. The Rasperry Pi command terminal is called LXTerminal (the Raspberry Pi Foundation has a nice intro to the Terminal, which can be found on: ).

It is recommended to update and install all upgrades for the OS before installing the necessary software. This can be done via Terminal using the commands below:

sudo apt-get update

sudo apt-get upgrade

(This may take several minutes to complete)

Once the update is done, power off the Raspberry Pi and disconnect it from the power line to
connect | the | camera | cable | to | the | camera | port | as | detailed | here:
https://www.raspberrypi.org/documentation/usage/camera/

The FlyPi runs on two pieces of software, one running on the Arduino board and the second on the Raspberry Pi. They are both described below.

Arduino
The code used to control the Arduino board, called a “sketch”, can be easily uploaded using the Arduino IDE. The steps to install it are better described at , in the sub-section “Install the Arduino Desktop IDE”. On the same website the steps necessary to upload sketches and check that everything is running properly can be found at the specific section for the Arduino Pro board https://www.arduino.cc/en/Guide/ArduinoPro.

To install the IDE, open a terminal (check the Running a terminal and installing software on GNU/Linux systems section) and type the following command:

sudo apt-get install arduino

If the LED ring and/or Matrix from Adafruit are going to be used, it is also necessary to install the respective Arduino Libraries, from the Adafruit repository: and

Setting up the Python Graphical User Interface (GUI):
Open up a terminal (check the Running a terminal and installing software on GNU/Linux systems section) and install the library required to convert “.h264” videos (standard output of the PiCamera) to “.avi” videos (that can be loaded by ImageJ and other analysis software). On the terminal type:

sudo apt-get install libav-tools

After the necessary libraries are installed, the GUI software can be installed. To do so, download the zip file from the GitHub repository and unzip it on the desktop

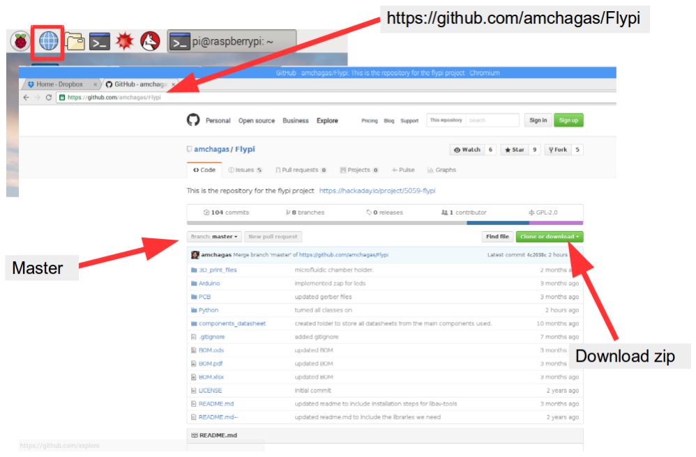
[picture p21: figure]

Now the system should be ready to run the GUI (see Starting the GUI section).

Method 2 (easy)

If the user has a reliable Internet connection with enough band, an “image” file, containing all software pre-installed can be downloaded and cloned to an SD card.

The disadvantage of this method is the necessity to download a 16 GB file and the necessity of having a 16GB (or higher) SD card.

Using a computer connected to the Internet, download the FlyPi image from this link (https://www.dropbox.com/s/394hf52xq9p3vuk/flypi.img?dl=0) (currently a dropbox folder, maintained by the developers and containing the most up to date version of the system) – and clone it to the SD card to be used with the Raspberry pi.

Installing | the | image | to | an | SD | card | is | better | described | here
https://www.raspberrypi.org/documentation/installation/installing-images/

After cloning the image, the SD card can be inserted on the Raspberry Pi and the system started.

Starting the GUI

Once everything is installed, the GUI can be started by opening up a terminal and typing:

cd ~/Desktop/Flypi-master/Python/

sudo python3 ./run.py

Data location and Remote control

All data generated by the FlyPi GUI (videos, snapshots, temperature logs, protocols) are stored on the desktop, in an automatically created folder “flypi_output”. Here, data is further divided into subfolders according to the data type.

To change the place where the data is stored (e.g., to a USB memory stick) locate the variable “basePath” in the file flypiApp.py and change it to the new location:

basePath = '/home/pi/Desktop/flypi_output/' (default)

basePath = '/dev/sdb/' (hypothetical location)

This tutorial provides information on how to locate the path to a USB memory stick on Linux systems.

To avoid overwriting files, files created follow this name convention: “Year-Month-Day-Hour-Minute-Seconds”+ extension (e.g., 2017-03-31-10-50-23.h264 for a recorded video).

Once all necessary software is installed, it is possible to control the FlyPi remotely, for example using a Laptop or Desktop computer. There are many useful tutorials online showing how to do this using different protocols (SSH, VNC). One example can be found here. (https://www.raspberrypi.org/magpi/ssh-remote-control-raspberry-pi/) One alternative is the use of software dedicated to this task, such as TeamViewer, (https://www.teamviewer.com/en/?pid=google.tv_ex.s.de&gclid=CJmZ2oHR9NMCFVEW0wodP-gNwg) which is free (for non-commercial use) and easy to setup, but proprietary.

## Electronics

The printed circuit board (PCB) will be populated with “through-hole” components. They are arranged in functional modules and their soldering order does not matter. Our suggestion is to start by deciding which modules will be installed and to start soldering smaller components (e.g. resistors, transistors), independent of which module they belong to, and move on to bigger components (integrated circuits, capacitors) afterwards. Another suggestion is to place all components in place and bend their leads on the bottom side of the PCB if possible. This will allow the user to make sure everything fits and is well placed before soldering.

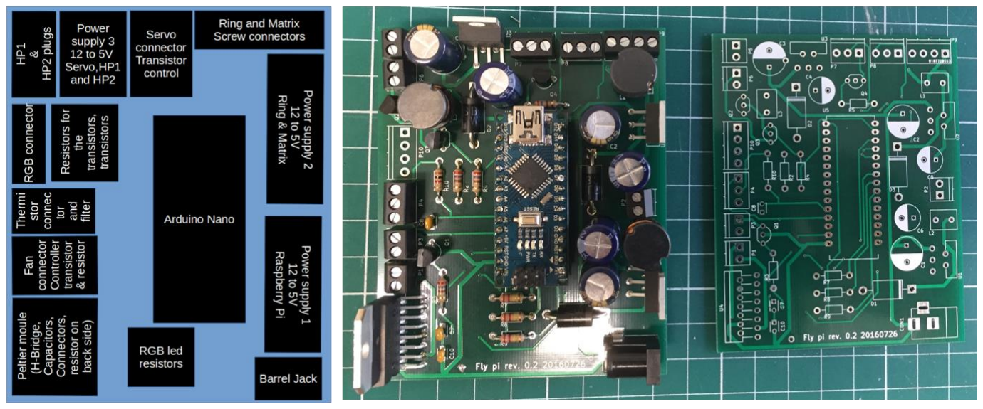
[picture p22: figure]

Arduino connectors
Plug the female headers to the Arduino board. Next, place the headers in the designated area on the PCB and solder only the edge pins (two per header). Disconnect the Arduino from the headers and finish soldering the remaining pins. This method ensures that the Arduino and the header pins will be aligned once soldering is done, and that the microcontroller won’t be damaged by the soldering heat.

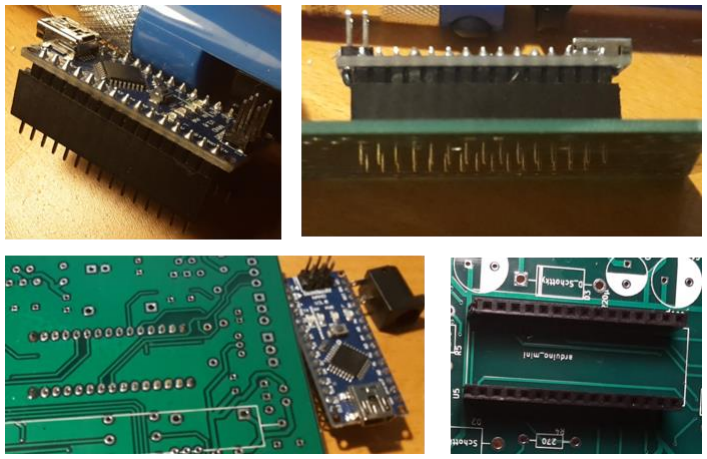
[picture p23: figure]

Raspberry Pi power line
The PCB contains a circuit dedicated to powering the Raspberry Pi (it converts 12V from the main input into 5V). This circuit is close to the barrel jack, and the main concern upon soldering the parts is the orientation of the capacitors and diode. Their position and value are indicated by the print on the PCB. Note: Larger capacitors such as these ones and diodes have a polarity – make sure to solder them the right way around. By convention, the “short” leg is (-) and should be slotted into the white part. Note that usually this is also somehow indicated by the writing/patterning of the component itself.

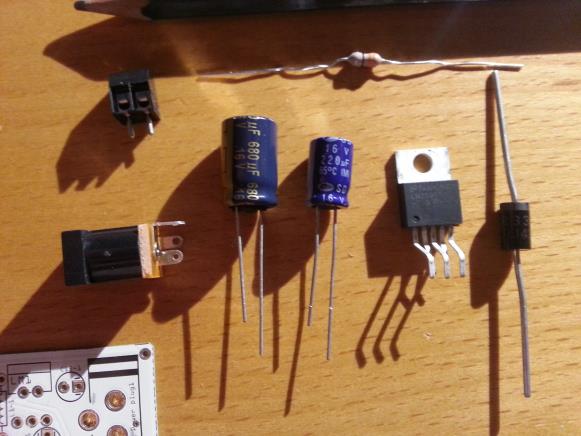
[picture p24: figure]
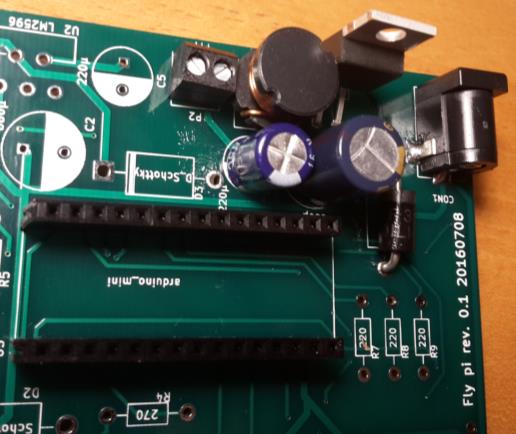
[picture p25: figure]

To finish the Pi power line, take the USB cable that powers the Raspberry Pi (A to micro B) and cut it close to the A part (the end that is NOT connected to the Raspberry Pi’s power port). Within the cable, there are four wires, two of which need to be exposed (and the others simply cut short). By convention, the red and black wires are positive (+) and ground (GND) power wires, respectively. Once stripped, they need to be screwed into the corresponding ports of the screw terminal as indicated.

Once the Pi power line and the Arduino connectors are finished, the system should be tested before any other modules are soldered. Plug the Arduino into the connector (USB port side on the opposite side of the Pi power supply), the USB cable from the PCB into the Raspberry Pi. Turn on the system by inserting the power supply plug into the PCB’s barrel jack. Make sure the Raspberry Pi cables (keyboard, mouse and monitor) are connected and the SD card is properly inserted before doing so. The system should boot up.

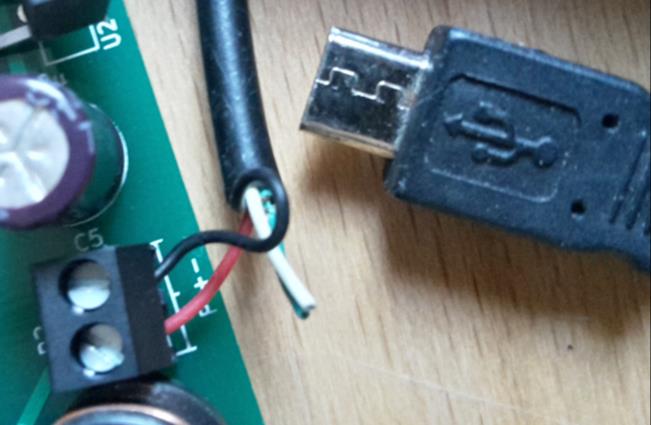
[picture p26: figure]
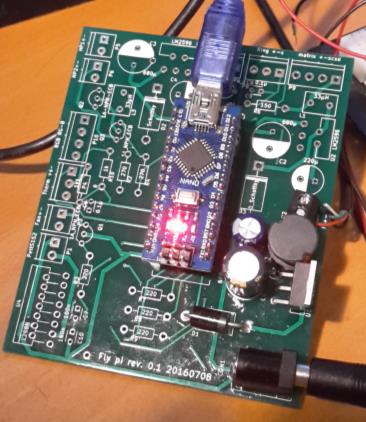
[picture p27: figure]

LED Ring and LED Matrix modules
The LED ring and the LED matrix share the same power module (composed of the same components of the Pi power module and located next to it), but can be installed independently from one another. WARNING: The LEDs are rather bright at full power – directly looking at them for too long could cause damage to your retina!

The power module and screw terminals should be soldered in the same way as the Pi power module (see above).

Solder 3 cables (~15-20 cm) to the back of the LED ring / diamond as indicated (+, GND, Signal). The 4th connector is left unattached. Care should be taken to not damage the LEDs by overheating the back of the array (it’s quite robust, but just in case). If both the ring and the diamond are to be used in tandem, the respective pins can be connected to each other (i.e. + to +, GND to GND, S to S) rather than using 6 long cables. Note, however, that in this mode the individual pixel control will not be straightforward. The entire array can however still be controlled as one without problem which will suffice for most applications. If desired, fix the diamond into the hole of the ring using tape or glue.

Care should be taken that the wires leaving the screw terminals on the PCB connect the correspondent place in ring and/or matrix.

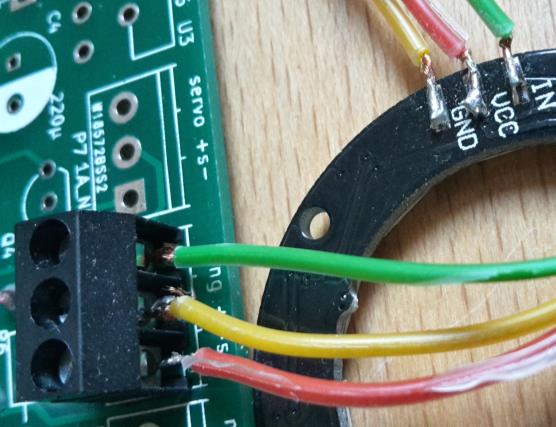
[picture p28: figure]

Peltier Module

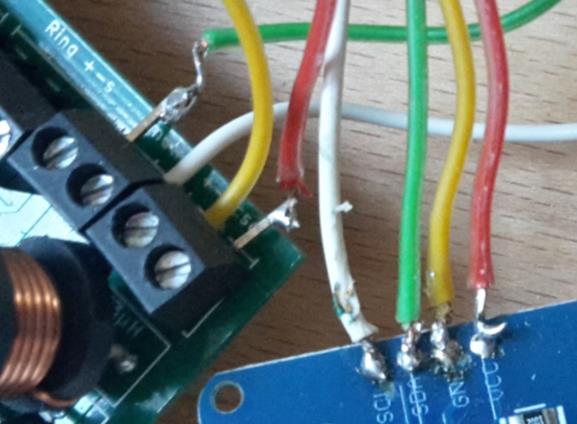
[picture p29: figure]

Start with the H-bridge (the tall component with 8 pins), making sure its flat side faces the outside of the PCB. Next solder the capacitors, making sure they are correctly oriented (short leg into white). Place the screw terminals (one for the Peltier itself and one for its cooling fan) and screw in the cables (orientation is also important here. The proper orientation is determined by the marks on the edge of the PCB). Last for the proper functioning of this module the high capacity resistor needs to be soldered on the back side of the PCB. Next solder the resistors for the RGB LED and its screw terminal. Last, place the capacitor and resistor for the temperature sensor and its screw terminal.

If the RGB and Thermistor are to be used (part of the Peltier module, or in case of the RGB LED also useful as indicator LEDs during “protocols” see GUI) solder 4 cables (~10-15 cm) to the 4 pins of the RGB-LED, taking note which cable connects to which pin. The longest pin is typically the anode, with the single pin next to it being the one for the red LED. The other two, in order, are green, then blue. If in doubt, applying a small voltage (e.g. from a multi-meter in “diode mode”) across the LED between the anode pin and one of the others should make the respective LED light up. Insulate the contacts to the LED against each other and slide some small plastic tubing (or heat-shrink/tape) over the assembly as indicated. The other ends of the RGB led cable should be connected to the assembled PCB as indicated.

The thermistor (optional) is assembled in essentially the same manner (with 3 pins rather than 4, of course) as the RGB led. The pins on the sensor are +, signal and GND, when the curved part of the sensor is facing down and the pins oriented towards the observer (check the sensor datasheet for more details: http://www.analog.com/media/en/technical-documentation/data-sheets/AD22100.pdf)

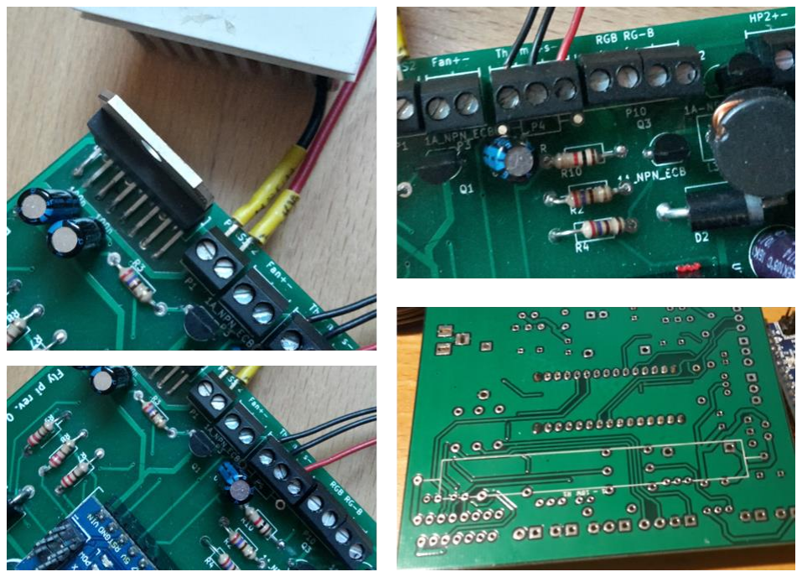
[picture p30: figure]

Servo and high power line module
The servo motor and the high-power lines (e.g. to drive the LEDs of the Fluorescence module) are powered by a third power module, exactly the same as the Pi power module and should be soldered in the same manner. This module has transistors, resistors and screw terminals as the remainder pieces. Start with the resistors and move on to the transistors taking care that they are positioned in the right way, with the rounded side aligned with the drawing in the PCB.

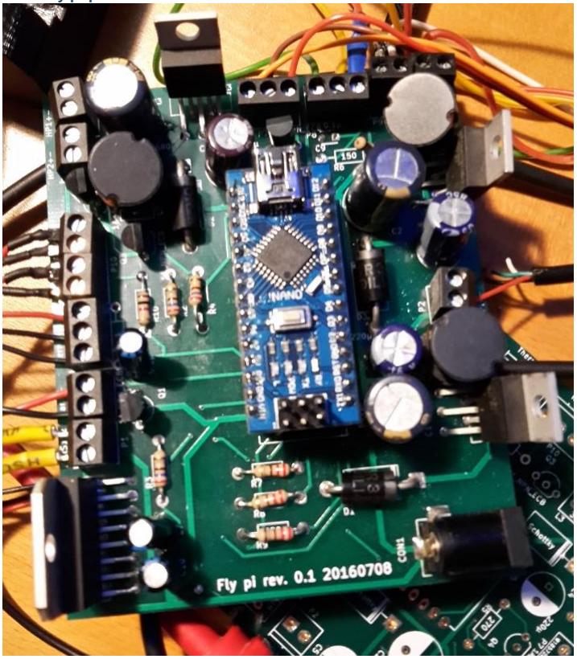
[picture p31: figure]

The fully populated PCB

## 3D printed parts

To print all the necessary parts, a printer with minimal print area of 200x200x150 mm should be available, as the longest part has a length of 223.5mm (place it at 45°if required). Alternatively, we suggest to print all parts that would fit the printer’s bed and use a print on demand service (there are several available at 3Dhubs.com) to print the remaining ones. If no printer is available at all then this option can also be used to source printed parts – this should come to ~40 € if using a low-cost service.

Mounting the camera
Option 1 (manual focus). Place the “Adjustable focus RPi camera” into the 3D printed holder as indicated. The camera PCB should fit easily and finish evenly against the top of the frame (back of camera). If not, file down the 3D printed part until it fits. Fixate camera in place e.g. with tape as indicated, optionally taking care that the integrated LED next to the CCD chip is blocked with tape (this can also be software-disabled if preferred). Next, slot an M3 screw of appropriate length fitted with a 3D printed thumbscrew (e.g. 12-20 mm) into the mounting hole.

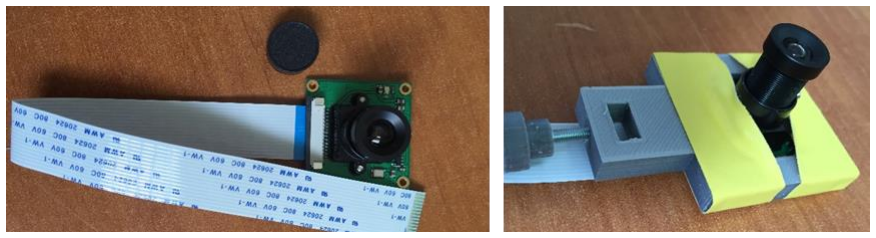
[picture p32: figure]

Option 2 (motorised focus). As above, but use the extended 3D printed Camera mount and locate the two 3D printed cogwheels. Place the continuous rotation micro servo through the slot next to the main camera mount, carefully noting its orientation as indicated, and fix in place using the screws provided with the motor (you should be able to just screw these straight into the 3D printed frame – predrill small holes with a Dremel or similar if necessary). Alternatively, the motor can be fixed with tape, or may even stay in place by friction alone. Next, fully unscrew the camera objective and fit the cogwheel without the X-shaped inside mounting slots over it as indicated. If it does not stay in place by friction alone, use a small drop of glue, taking care that the objective lens remains clean. Next, locate the X-shaped mounting adapted that comes with the motor and slot it inside the remaining cog-wheel as indicated, again taking careful note of the orientation (the motor will be attached from the same side). Again, use a small drop of glue if the X-mount does not stay in place by itself, carefully ensuring centring. With the camera module mounted as in Option 1, screw the objective back in and complete the assembly by slotting the motor-cogwheel over the motor. The cogs should turn easily when rotated by hand with only the servo resistance blocking motion. If not, carefully check alignment and file down the cogs slightly as required.

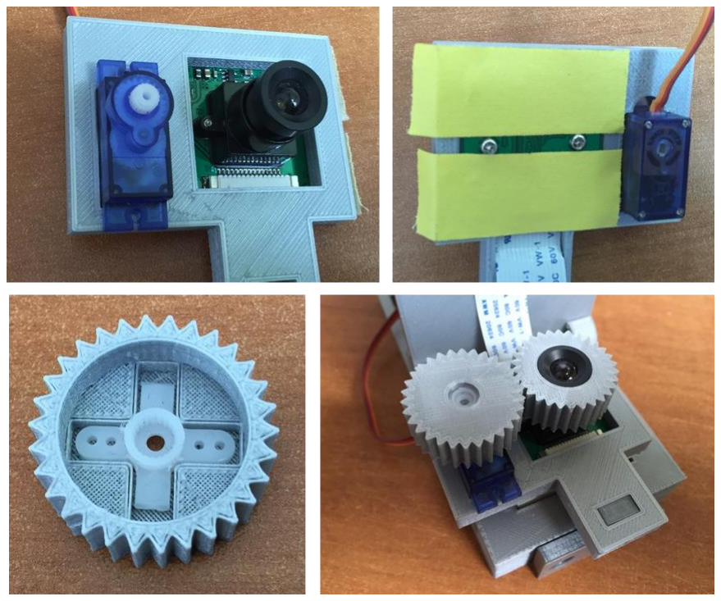
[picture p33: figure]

Assemble the Peltier Element with heat dissipation
If a Peltier Module will be added, place a generous amount of heat-conducting paste on top of the heat-dissipater (the flat side). In addition, place a small amount of glue to the 4 corners of the same face and glue everything centrally to one side of the Peltier element (either side is fine – just swap the red and black wire connectors on the PCB if it turns out to be “inverted”). Make sure the glue is set before proceeding. Leave the CPU fan aside for now, this will be added at a later stage.

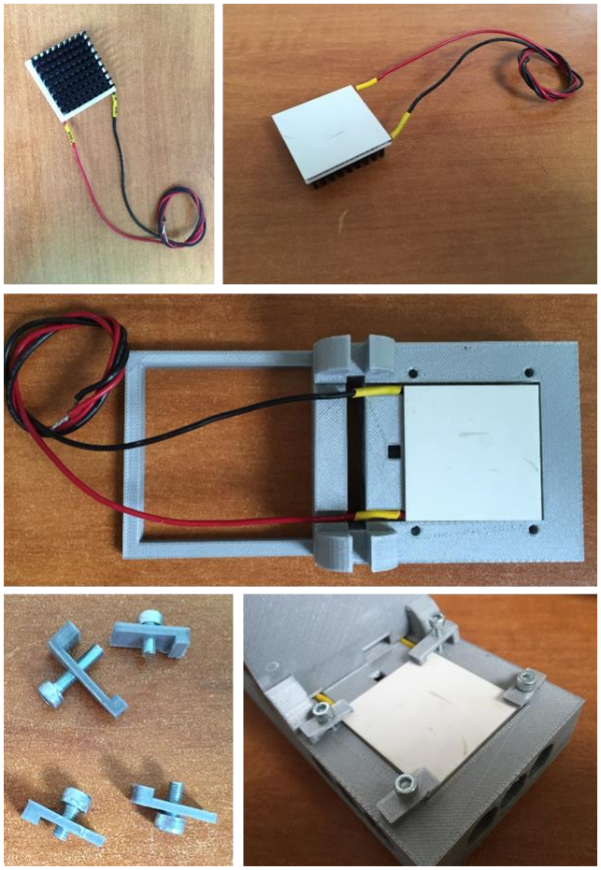
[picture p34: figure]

Mounting the RPi onto the main wall-plate
Lay the 3D printed wall-plate flat against the table with the screw-mounts facing upwards and orient the RPi2 on top. It should fit precisely with all 4 screw-holes aligned. Locate 2 12-16 mm M3 screws and loosely attach the top 2 holes (by the USB ports) as indicated. Next, locate the 3D printed PCB mount and place it on top of the remaining 2 screw-holes such that all holes are aligned. IMPORTANT: Carefully check that the part of the PCB mount that touches the RPi2 will not squish any protruding elements of the RPi2. If there is slight overlap, file down the concerned part of the PCB mount before proceeding. Then take the two long M3 screws (~30 mm) and mount everything together as indicated. Also tighten the top 2 screws previously inserted.

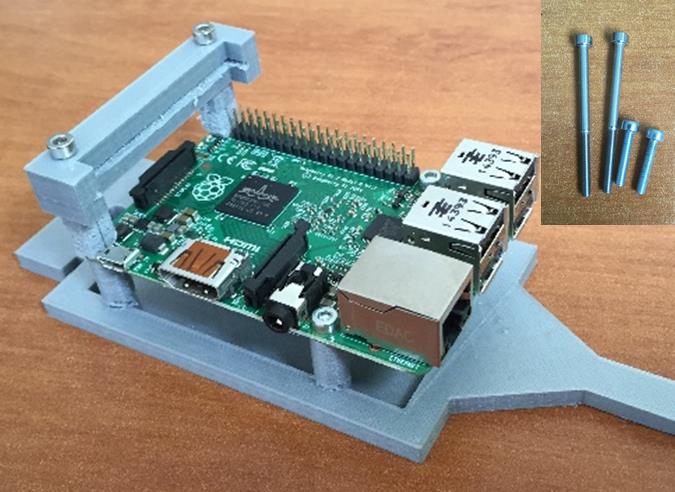
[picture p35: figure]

(note that the picture shows an outdated version of the PCB holder mounted on top of the RPi – the current one is a bit wider)

Mainframe
Option 1. With Peltier Element. Place the assembled 4x4 mm Peltier element with heat dissipater below (Part 4) into the 3D printed base as shown and clamp down with 3* x mm screws and the 3 shorter 3D printed Peltier clamps. The 4th, slightly larger clamp will be mounted with a longer M3 screw in the remaining slot as indicated. This will eventually hold the Thermistor in place. Next, slot the assembled wall-plate (above) into the base with the RPi2 on the back as indicated. Make sure the Peltier cables slot easily though the lateral slits provided (you will have to simultaneously slot in the Peltier cables and wall-plate). Next, mount the camera. For this, slot the ribbon cable into its plug on the RPi2 and fix in place using the “clip” that comes pre-attached to the RPi2. Slide the Camera over the wall-plate’s turret and fix in place for now using the thumbscrew. Finally, slot the fully-assembled PCB into the mount as indicated and connect the Arduino to the RPi2 using the USB cable provided. By default, the FlyPi scripts are configured to expect the Arduino to be connected in its nearest USB slot (central, upper).

Optional mounting turrets or a 3D printed micromanipulator can now can be slotted into the front or side faces of the base as required.

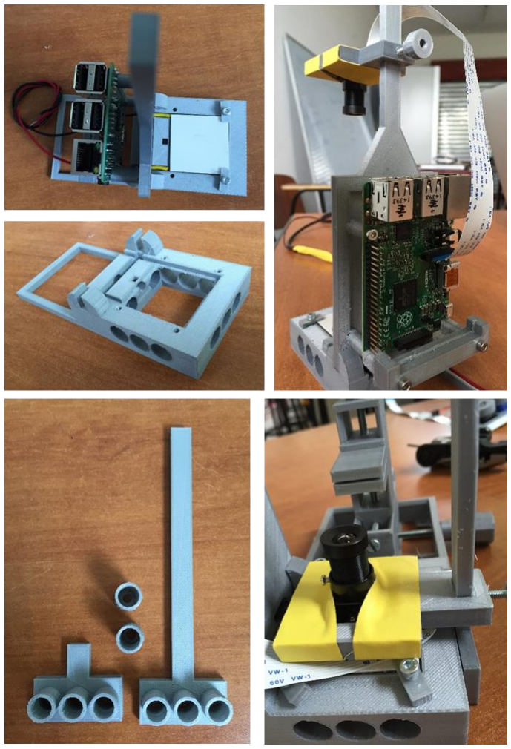
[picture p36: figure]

RGB-LED and Thermistor
The RGB LED can be slotted through the back of the base/wall-plate as indicated until it is clearly visible through the hole from above. (Of course, depending on the final application of the FlyPi, the LED can be positioned in any number of ways.)

The temperature sensor is slotted through the slightly larger and elongated slot in the wall-plate as indicated.

Peltier Fan and “Feet”
To better dissipate the heat of the Peltier it can be helpful to add a fan. This is simply placed beneath the Peltier, while the FlyPi is propped up by 3D printed feet. Note that there are also “feet” available for the micromanipulator if required.

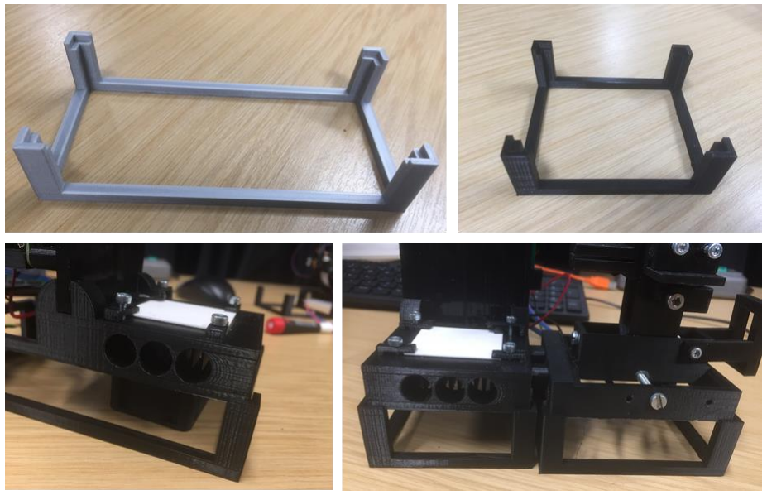
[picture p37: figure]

In its most basic format, this completes the FlyPi assembly. In the below, we now describe the assembly of the various optional modules that can be included in the build.

NeoPixel LED ring / Diamond / Matrix
Place the ring into the 3D printed holder, noting the orientation of the small protrusions relative to the widenings in the mounting adapter. Slot the cables through the hole in the neck. Finally, fix the LED ring in place using tape. The other end of the LED ring cables are connected to the main PCB as indicated.

For the LED Matrix, follow the simple instructions online on Adafruit website (https://learn.adafruit.com/adafruit-led-backpack/), slot it into the 3D printed mount and connect to the PCB as indicated.

Finally, if required, prepare “diffusors”, e.g. using the milky-white weighing boats glued into place in the 3D printed mounts provided. Alternatively, plain white paper acts as an efficient diffusor as well (but be careful not to burn the paper, the LEDs can get hot), as does any other milky white plastic or a Teflon screen (e.g. plastic milk bottles as used in many countries work great). Two diffusors separated by a few mm are particularly effective (not shown).

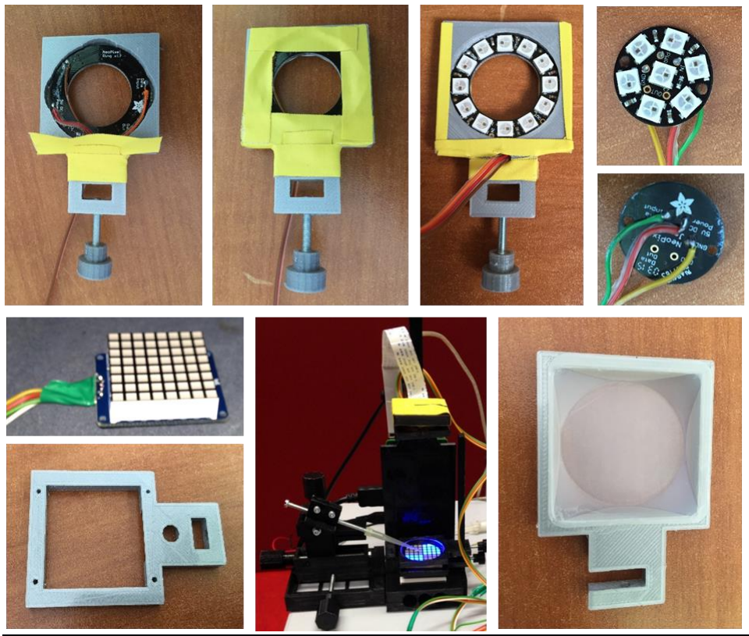
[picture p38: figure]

Fluorescence module
Begin by attaching (+) and GND cable connections (10-15 cm) to the high-power excitation light LED (not shown). Next, attach the reflective collimator on top of the LED and fix with a drop of glue and fix a small piece of the blue Roscolux filter (“Baldassari blue”) on top of the collimator (seen only in subsequent image here). Take care that the glue does not spread over the filter. Now add a drop of heat-conductive paste to the back of the LED and glue everything onto the flat face of a heat-dissipater, assuring that everything is as well centred as possible (note that in the images provided, the cables are not attached yet by accident – this makes it much harder to solder on the contacts as the heat-dissipater will dissipate the heat from the soldering iron). Next, slot the excitation LED mounted on top of the dissipater into its mount as indicated, and slot everything on top of one of the tubes of the main unit that is angled at 45°. Proceed identically with an optional second excitation LED light source for the other 45° tube (not shown). Any remaining open tube ends should be plugged with the lids provided to block light. Note that it may be handy to leave the vertical tube optionally open/closed as this can be used to transmission illumination using the room lights or the LED ring in tandem with the fluorescence mode - so don’t glue the lid in place. Excitation LEDs are attached to the slots provided on the PCB. WARNING: The UV LED is very bright and poorly visible to the human eye (i.e. it is much brighter than it looks!) – directly looking into it can seriously damage your retina!

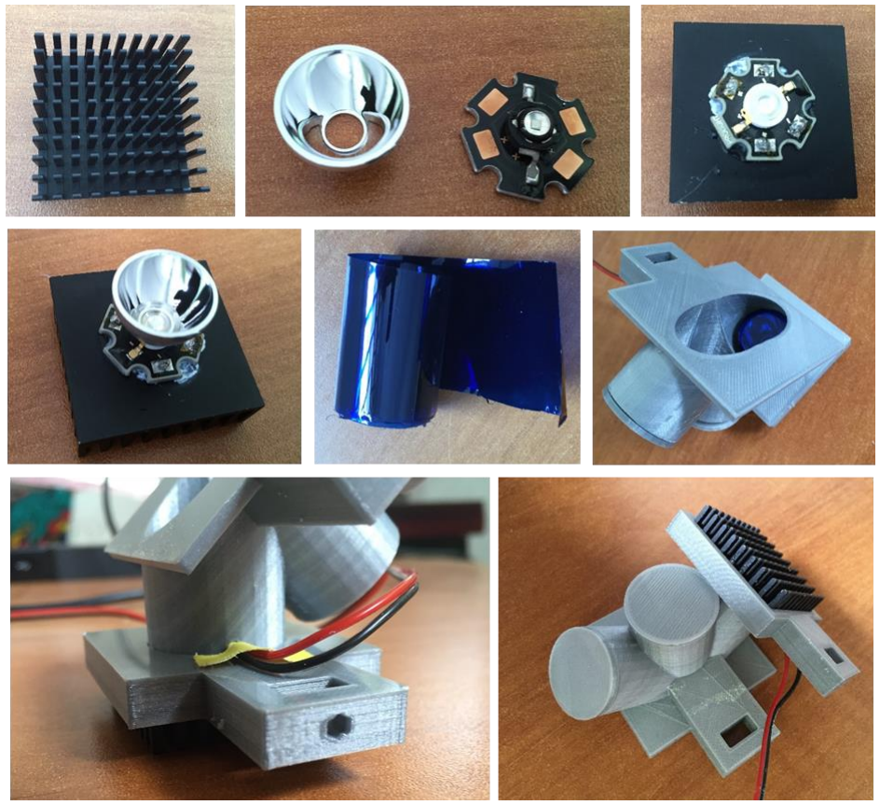
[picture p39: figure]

For the filter-wheel, first cut small pieces of Roscolux filters appropriate to just cover a single hole of the wheel, and glue them in place on the underside (the side with the pin) as indicated. Take care not to smudge the filter that covers each hole with glue. Next, plug the filter-wheel’s pin into the mounting adaptor as indicated. If the filter wheel comes loose, try slightly heating the pin as it comes through the mounting adaptor’s pin hole as to slightly expand its end and thus fixing it in place (e.g. using lighter, or by holding the soldering iron near it without touching). Be careful not to burn the filters which can happen quite easily in this step. If everything is too tight, file down the central pin until it fits well.

Finally, attach thumbscrews to both excitation mount and filter wheel and put everything together.

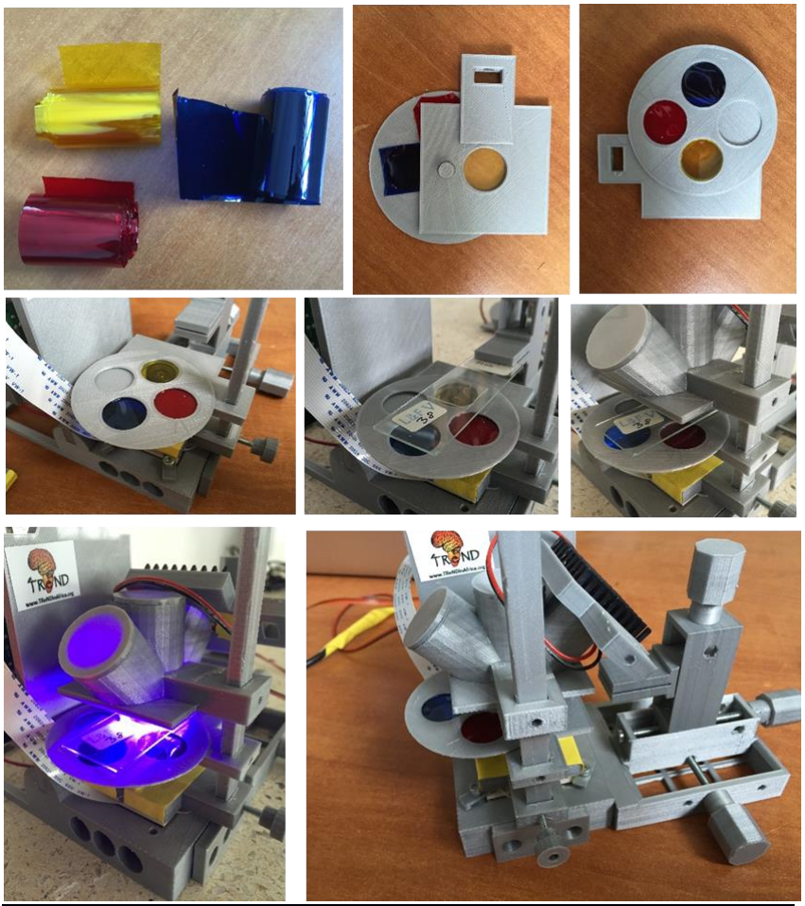
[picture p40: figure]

Petri dish mounts and fly behavioural chamber
The lid-part of standard small and medium sized petri dishes should easily slide into the 3D printed petri-dish mounts and should stay firmly in place without need for further fixation. Attach to mainframe for the FlyPi using thumbscrews as usual.

The Fly-behavioural chamber consists of 2 standard glass microscope slides and 2 3D printed parts as indicated. Simply glue the back face of one of the 3D printed parts to one of the glass slides, then glue the other 3D printed part on top as indicated. This should create a slot through which the other glass slide can be optionally inserted to form the lid of the chamber. Note that the chamber is made from glass rather than plastic as not to filter blue/UV light which may be useful e.g. for optogenetic stimulation. Note also that the STL file collection also contains a design for equivalent mounting plates for double-size microscope slides.

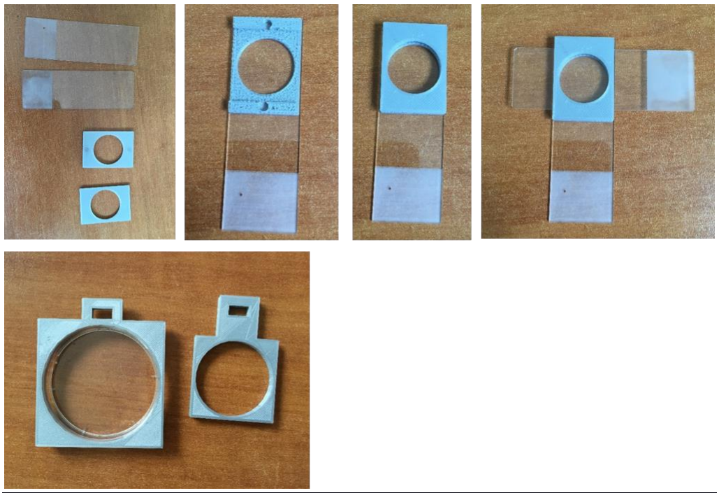
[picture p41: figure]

Any issues with 3D printed parts?
If any 3D printed parts do not seem to fit etc, it can be worth looking at the original OpenSCAD file (Need to download OpenSCAD which is freely available at www.openscad.org ). In the code, each piece is built from a single or multiple “modules” which can be edited. Most key parameters are variables with hopefully self-explanatory names.

One Key parameter is the “Tol” one in line 38. This is a global parameter that is added to all sliding parts, and defines, in mm, the size of every sliding gap. If the pieces are all too tight, try increasing this to e.g. 0.1 (or even 0.2 for a less accurate printer). After any modification, the model needs to be compiled again (F6) and exported as STL for printing. Note that there are several switches in the top that allow switching on (1) and off (0) individual pieces of the model.

Micromanipulator assembly and motorisation

This is described in detail elsewhere:

https://openlabwaredotnet.files.wordpress.com/2015/11/manipulator-assembly-instructions.pdf

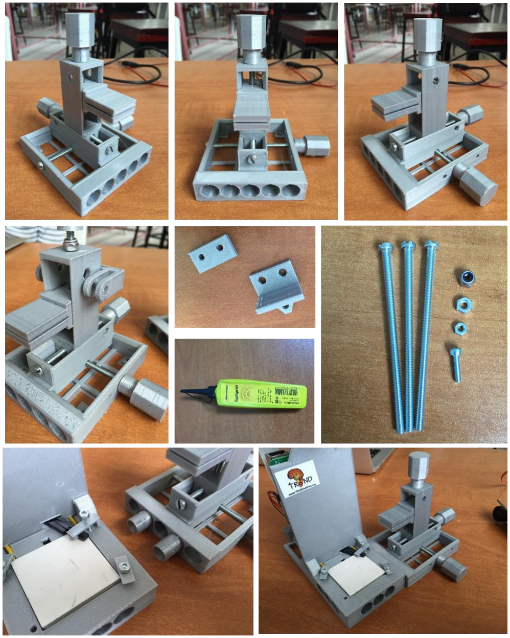
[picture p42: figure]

## Operating the Graphical User Interface (GUI)

Activating / Deactivating individual parts of the GUI
The GUI is organised in a modular fashion: Camera, LED1, LED2, LED Ring, LED Matrix, Peltier, Auto Focus and Protocols. Each module can be activated and deactivated as required. To do so, edit the file named flypiApp.py and find the variables named xxxxFlag (e.g., cameraFlag). Setting them to zero/one will switch off/on a module, respectively. For users who want to create their own modules, a new file containing a Python class with all necessary methods and variables should be generated, as well as a similar variable in the XXX file, as described above. For more details, please refer to “mock_up_module.py”

Camera control
The GUI provides for simple access to most built-in camera control options. Some of them, such as Resolution, White Balance, Mode and Colour Effects are controlled via “dropdown” buttons which continuous parameters are set via sliders. This module also provides a subsection for recording data from the camera: The button “video” records “h264” video keeping all settings changed by the user, except resolution, as there are limitations on the PiCamera library, when using maximal resolution (2592X1944). The duration of the recording is set in the box “DUR (sec)”. The “timelapse” button takes still photographs every “INTERVAL (sec)” seconds for a total of “DUR (sec)” seconds. The “photo” button takes one snapshot. In both cases (timelapse and photo) images are recorded in “jpeg” format

LED control
There are 4 different LED related panels.

The first two control the high-power LED slots as used e.g. for the fluorescence module. An “ON” button turns the respective LED on until the “OFF” button is pressed. For automated timing a “Zap” control is present, where the user can define the LED activation time (in milliseconds) that is counted down upon pressing the “Zap” button. Notably, these ports are general purpose and could be used to control any <=5V element as required (motors, lights etc.). To set a port to the “right” voltage, it may be necessary to switch the resistor positioned next to each port (cf. circuit diagram on GitHub).

The LED-Ring panel has the same interface as the high-power LEDs, with the addition of extra controls to adjust the intensity of each colour channel (Red/Green/Blue, for spectra see Fig. 5B). In the “Zap” controls, this allows for the ring to be on with a specific colour combination, and have a different colour combination “zapped” for a specified amount of time. To control the colour combination for the steady ON state, four different sliders are provided, one for each of the RGB channels and one that controls all channels together. To control the colour of the light “zap”, the user should input numbers in between 0 and 255 into the text boxes (“red flash”, “green flash” and “blue flash”). Notably, Adafruit produces many different shapes and sizes of these so called “NeoPixel” LED arrays, most of which are directly compatible for FlyPi without reprogramming (e.g. all rings and the “diamond”).

The Matrix panel has a different configuration. Here an “OFF” button is present, together with 3 “ON” buttons for different pre-programmed patterns, and a slider that controls the brightness of all LEDs present in the Matrix. Each “pattern” button is pre-configured to generate a specific light pattern, which can be static or dynamic. To change the pre-programmed patterns, update the annotated pattern-related code segment near the top of the Arduino sketch and re-upload it to the Arduino. For more information on how to programme Matrix patterns, the user is referred to the excellent tutorial section on the Adafruit website ().

Peltier control
The Peltier control consists of “ON” and “OFF” buttons, a slider to set the desired temperature and a checkbox for enabling/disabling temperature log (into an asci file). Once the “ON” button is pressed, the temperature command on the slider is transmitted to the Arduino. The temperature slider can be changed at any time, and the final temperature on the Peltier surface is held by a closed loop system between the Peltier current control (an H-Bridge in this case) and the temperature sensor installed on top of the Peltier. If the “OFF” button is pressed, current to the Peltier is interrupted, but temperature changes still occur as the device temperature equalises with room temperature. If the checkbox “Log temp?” was marked during the Peltier use, a file will be created and the readout of temperature sensor.

Note1: if the Peltier polarity is switched (i.e. if it heats rather than cools and vice versa) the red and black wires as plugged into the PCB need to be swapped.

Note 2: As one side of a Peltier cools by a certain degree, the other side will inevitably heat up to a greater degree, leading to an overall increase in temperature. It is therefore possible that at some point the Peltier will fail to cool to the desired temperature. If this happens, make sure a fan is positioned under the Peltier as shown in Fig. 6 – this will help to dissipate the heat. If this is still not sufficient, consider the ambient room temperature – putting the entire system in a cooler spot can dramatically increase overall performance.

Auto Focus
Auto Focus controls a continuous rotation servo motor attached to a gear system connected to the lens above the Pi Camera. Moving the slider to one direction will make the motor turn clockwise, and in the opposite direction counter-clockwise. The more the slider is displaced, the faster the motor movement. Since the camera does not require the motor for focusing and operating, users can adapt this module to their own specific needs (e.g., opening and closing physical barriers or to drive an optokinetic drum).

Protocols
This module is designed for automating stimulation and recording procedures. Each column is executed sequentially and for the time set in “Dur(ms)”. Once all five columns have been executed, the program waits for the time specified in “IRI(ms)” and thereafter repeats from the first column for the number of loops defined in the “Repetition” box. If “camera” is set to “ON” a video will be taken throughout the execution (to avoid system crashes, the user is advised to make sure that the SD card has enough space to record all data). If “camera” is set to “OFF” the protocol is executed without recording video, which is useful for testing or recordings using external devices. In case the Peltier is being used and the “log temperature” checkbox in the Peltier module is checked, a text file containing a timestamp and the read temperature will also be created.

Note: As the protocol execution is controlled by the Arduino microcontroller (rather than the RPi), time precision achieved at the general purpose LED ports is the order of microseconds. However, since the LED/Matrix ring relies on a multiplexed signal from the Arduino which is executed through the Adafruit library only at 100s of Hz, its precision is slightly lower (~5 ms).

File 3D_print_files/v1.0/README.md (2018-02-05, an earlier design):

# Notes on `FlyPi_v30.scad`

## _Caution_

These parts have _not_ been printed to verify the design.  Although the design
has been checked carefully, it is possible that some parts may not function
as desired.  No warranty for any fitness of use is given or implied.

## Viewing modes

The design may be viewed in two different modes:

1. `EXPLODED_VIEW`: shows how the parts relate to one another in normal use.
2. `PRINTABLE_LAYOUT`: used to reduce the labour costs during printing by
 allowing multiple parts to be printed at the same time, and to be printed in
 an orientation compatible with fused filament fabrication.

The current view is controlled by setting the `assembly_location` variable near
the top of the file to equal either `EXPLODED_VIEW` or `PRINTABLE_LAYOUT`.

## About batches

There are variables that enable the printing of parts in batches.  
Batches are sets of connected parts that lie flat on the Z = 0 plane
and they are oriented to be printable with fused filament fabrication.  
Connection "wires" tie parts together, reducing the labour costs for printing.  
These connection wires should be cut off after the parts have been printed.

There are currently three batches of parts, and most of the parts in a batch are
related to each other. When viewing in `PRINTABLE_LAYOUT` mode, the current batch
is controlled by the `printing_batch_number` variable; this variable is ignored
in the `EXPLODED_VIEW` viewing mode.

The size of a batch is determined by the maximum printable volume, which is set
by the `max_print_bounds` variable near the top of the file.  The value of this
variable is currently set to the bounds for PLA printing supported by [Shapeways](https://shapeways.com).  
For those bounds, there are 3 batches.

To facilitate the placement of parts for the printable layout, the variable
`CHECKING_LAYOUT` may be set to `true` to show the X-Y profile of the printable
bounding box.

## Camera mounts

There are two different camera mounts supported, with and without servo motor
support.  The variable `use_servo_focus` controls which one of these is incorporated in the
design when the `show_camera_mount` variable is set to 1.

If `use_servo_focus == true` then the two gears that are used in conjunction with that
mount are also constructed.  A third party library, MCAD, is used for the
gear design, so that gear tooth shape is the involute form.  The pressure
angle was chosen to be 20 degrees but this may need to be changed.

## Selection of parts

Parts may be selected for construction in either viewing mode by setting the
switch variables at the top of the `FlyPi_v29.scad` file.

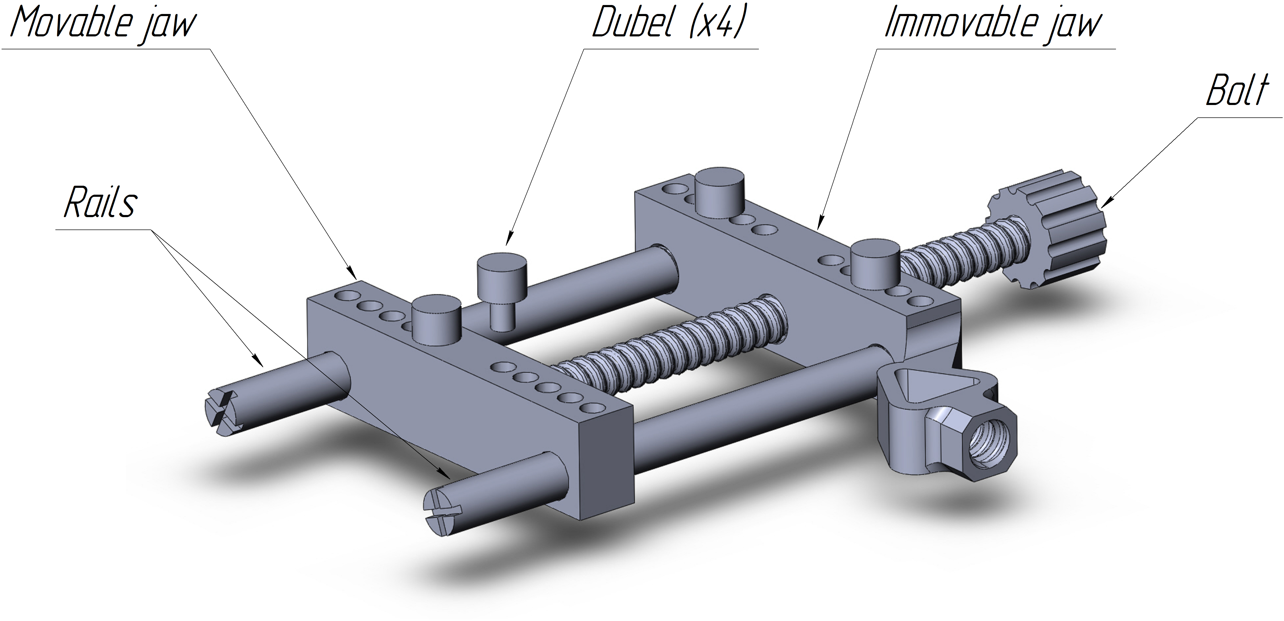
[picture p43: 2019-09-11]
3D_print_files/v2.0/STEPs/vise/vise_structure.png

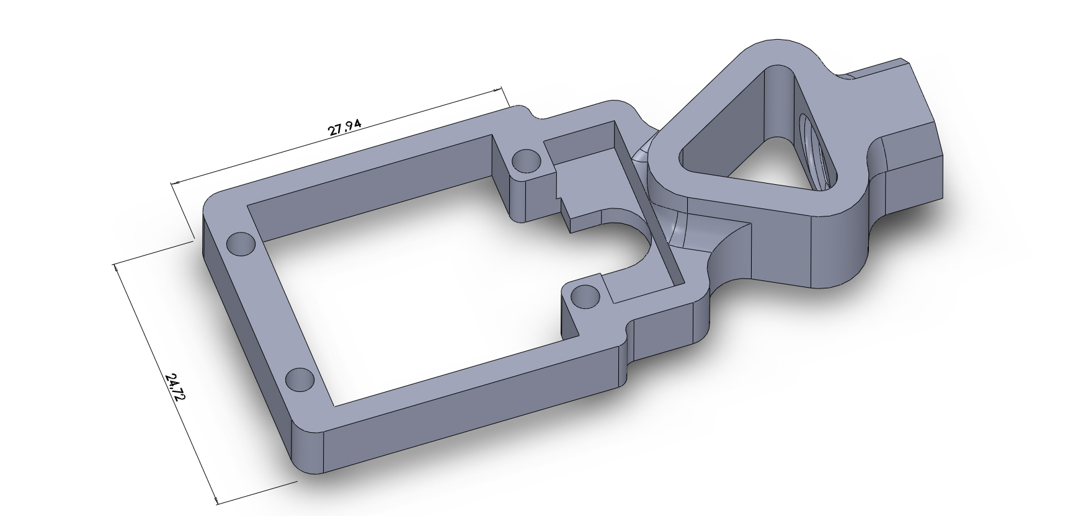
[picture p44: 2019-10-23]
3D_print_files/v2.0/STEPs/sobianin/LED_holder/LED_holder_rectangle_0.8.JPG

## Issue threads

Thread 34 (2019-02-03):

amchagas/Flypi #34: Make PCB Modular

amchagas, 2019-02-03:
Currently the system has 1 PCB containing all hardware modules. Optimally, each module would be implemented in a small PCB, as a piece of a puzzle. Seeed has implemented something like this with their [grove system](https://www.seeedstudio.com/category/Grove-c-1003.html). 

The advantage of this modularity would be to reduce costs (as users only need to source parts for the modules they need and each PCB will be smaller). Also it will allow bigger customization as users might want 3 LED modules and no Peltier module (as opposed to the stock 2 LEDs and 1 Peltier).

isobianin, 2019-09-23:
Hi! So I addressed this issue later and came with a plan of solving it. Nothing special but it will help with keeping this issue transparent to those who are interested in it and it just keeps everything organized. Additionally, it may help with estimating time needed to achieve desired result.
Plan of work:
1. Look into schematics and PCB layout.
2. Examine analogous systems.
3. Work on modularity.
3.1. Design new PCB layout.
3.2. Check PCB signal integrity and electromagnetic compatibility (Verify PCB's ability to function in general).
In order to accomplish set goals I would like to know the following:
1) This issue was posted a long (relatively) time ago. Are there any time restrictions? 
2) How is PCB assembled and manufactured? I suppose that you order it in assembled state from somewhere.
3) What components are available? There should be a little database where one can find required connectors and other components.
4) Even so I had looked through the folder "PCB", I got confused a little bit because there are so much files. Can you please explain what are the files that I can work with? I mean, what are the files for latest PCB schematic, layout and bill of materials?

amchagas, 2019-09-30:
Hi!
Thanks for putting some time and effort in thinking about this. 
Here are answers in order:
1 - no time restrictions, this has been a plan when this project was more active, but it went to the "back burner" as other priorities popped up.
2 - Never ordered it as an assembled piece from anywhere. we mostly get PCBs from pcbway or jlcpcb and use kitspace.org to get components. https://kitspace.org/boards/github.com/amchagas/flypi/
3 - all the components are here https://github.com/amchagas/Flypi/blob/master/PCB/flypi_pcb_kicad/1-click-bom.csv
4 - here are the latest files: https://github.com/amchagas/Flypi/tree/master/PCB/flypi_pcb_kicad

isobianin, 2019-10-01:
Hi! Okay, thanks. This information sorts some things out. I will try to post here updates on current progress and relevant questions

isobianin, 2019-10-21:
Hello @amchagas !
Sorry for the delay, here is an update. It contains some questions and propositions on the future design.

At first, I have found some info on this PCB in general (fig. 1). 
[image]
Figure 1 - FlyPi structure
It consists of:
a) power 1 - 12v to 5v converter dedicated to power the Raspberry Pi
b) power 2 - 12v to 5v converter to power LEDs, LED ring, Thermistor and devices on the I2C port
c) High power LED / 5V general module 1 
d) High power LED / 5V general module 2 
e) LED ring module 
f) servo motor module 
g) Peltier element module 
*) also there is SD card (I2C port)

The question is whether should all this stuff be modular? It is possible to do each module but I suppose things like power converter a) and b) will always be on this board. On the other hand, there are LEDs, servo motor and Peltier element module. LED ring is represented by one small plastic socket so I do not think that it is a problem to leave it there. 

Then there is a question of how can modularity be implemented? I see two main ways:
1) small PCBs are connected to main PCB via pin headers. This way the end result will look like mother board
2) small PCBs are connected to main PCB via wires through plastic sockets (just like LEDs and other instruments are connected to PCB now but new elements will be added to the current structure)

The first design may have different approaches:
- PCBs are placed perpendicularly to the main PCB (fig. 2)
[image]
Figure 2 - Perpendicular
pros: approach uses Z-axis and allows for more things to placed
cons: PCB enclosure is very tight and PCB may have problems with dimensions (for now, I have checked that LEDs can be implemented that way but more research is needed)
- PCBs are placed on top of the main PCB (fig. 3)
[image]
Figure 3 - On top
Pros: straightforward, relatively easy design
Cons: approach creates a lot of unused space below modular PCBs
- PCBs are parallel to each other (fig. 4)
[image]
Figure 4 - Parallel
Pros: relatively easy design
Cons: PCB will be cut, best used only on border modules (power, peltier), LEDs – not so much

Of course, it can be mixed. For example, LEDs are placed perpendicularly, big modules like power converters and Peltier are connected in parallel.
The second design probably should have some form of an enclosure. It may look like a box that have shelfs for PCBs (fig. 5).
[image]
Figure 5 - Enclosure

There are some questions on schematics:
1) there is a small discrepancy and capacitors C1 and C2 are mixed up
2) why is Arduino powered from CON1 Barrel_jack directly? There are no converters and 12 V (presumably) connect to the 5V pin.
3) maybe, if we are to make some changes in layout, we may increase the total number of LEDs that can be connected? I see that there are some pins that may do the thing. Also, we can add additional register and have even more LEDs

My vision of the solution is the first approach with pins and make it solely perpendicular (fig. 6). Try to do it this way or make it mixed.
[image]
Figure 6 - Design
What are your thoughts on amount of modules, design approaches and schematics?

P.s. There is a question in the issue #47. I have created the pull request because I have not recieved an answer yet

amchagas, 2019-10-23:
Hi @isobianin, very sorry for the long delay!!! 
I was travelling for work these days.
I like design 1 (figure 2) and variant B. You are also right to say that some things will always be there, such as the power modules on the right of the board. 
1 - I don't quite get what you mean with the capacitor discrepancy. Do you mind trying to explain it?
2 - The arduino is powered this way, because that is a volt_in port. And from the arduino datasheet, it can take up to 20V. (check power section on documentation tab here https://store.arduino.cc/arduino-nano). This was done this way to avoid draining too much power via the raspberry pi (as the other option would be for the arduino to be powered by USB)
3 - I wonder if we would be better thinking about this ports/spaces for small PCBs not as leds, but as "general" ports? I mean, the main PCB would have "ports/pcb connector" that would be three pins basically power/ground and data. and then each smaller pcb could be designed/configured for whatever function, including new things? In that way this would also be flexible enough to simply add cables if wanted/needed instead of the small PCBs?

isobianin, 2019-10-24:
Hi @amchagas, no problem, hope the business trip was successful.
1 - It is that identification numbers of capacitors in the schematics and in the layout are mixed up (fig. 1). It is a small detail that I had noticed and were puzzled at first.
[image]
Figure 1 - Discrepancy in components
2 - Got it, very informative. I knew that there was something with the pins' specification. 
3 - Totally agree with the first part of the paragraph. I was about to propose something like that because it is practical to design universal module that can be easily programmed. It just need to have enough pins. However, I did not quite understand the other part of the message. So are you referring to the second design where the main board consists of plastic connectors (or pin headers) which are connected to anything with the corresponding pins? In this case, what about driving circuits (transistors)? I mean there are examples without drivers on the same main board.
[image]
Figure 2 - Drivers
I came up with the idea of implementation of small PCBs based on an assumption that all the stuff on the main board is essential for its connection to the desired object (led, servo motor, led ring etc.). If the desired object resembles complete module (with all necessary driving elements), it is possible to replace small PCBs with connectors. Nevertheless, peltier will still remain as the one big module that, in all likelihood, will be turned in to the PCB.
Here I drew general concepts (fig. 3).
[image]
Figure 3 - Concepts
The A concept is what I was going for. The main issue of the B concept is the driving circuit. If it can be omitted, then it is settled and general-purpose connectors will be inserted on the main PCB.

isobianin, 2019-10-29:
Hello @amchagas! I see that we are still in phase of discussion of how general ports should look (small PCB or just ports). Therefore, while we are deciding what is better, I want to start designing the separate PCB for Peltier module due to the fact that we have already agreed on this particular module design. My algorithm is following: I will try to connect this module and main module via 90° pin headers. If the size of the designed PCB is too big for the enclosure and the main board, I will report it and discuss possible solutions

amchagas, 2019-10-29:
Hi @isobianin ,

1- Thanks for spotting that! 

about the last point, I was just wondering if we should think about a more general solution. Exactly in the lines of what you proposed with Concept A and B. Or like I mentioned in the first topic of this thread, like the grove connectors from Seeed studio. So in this way the main board would only have the power supplies and the arduino board. 
The rest would be a system/connector(s) layout for people to connect small PCBs containing different circuits? I don't know yet if this makes sense, given the many breakout systems that are already available out there.... Also I don't know how much sense would it make to keep changing this FlyPi design. Would it make more sense to keep this one as is, and move on to a new repo/project where we can have more freedom to test things? For instance, why not use an ESP32, that has more connection ports or even wifi, so that we have a more general system for different applications?

isobianin, 2019-10-29:
Regarding breakout systems, I think that we need to identify what makes FlyPi uniqe. What I understood during the given period is that it is more like DYI thing with through-hole elements and with a set number of modules, thus making it a bit cheaper alternative to, say, the Grove system. I would also point out that FlyPi is designed specifically for microbiology. This way it is more preferred by researchers to buy FlyPi than general-purpose PCBs. Probably, there is more to it but that is all I can say for now.

Speaking about new project, yes, this is definitely a better way of upgrading FlyPi and creating something more than it is now. New microcontroller would be a nice addition.

My opinion is that FlyPi is an existing project. If it exists then it is needed in some specific research areas. Therefore, an upgrade is likely to be a welcome addition

isobianin, 2019-11-04:
Hi @amchagas ! I spent some time thinking about the completely new layout of PCB we had discussed earlier. Probably, the best case would be to implement modularity, as you suggested, via small PCBs connected through cables. This way we can create the small set of PCBs that is specifically design for FlyPi project subject area (microbiology) so people are able to use them with their current breakout system (fig. 1). If they do not have one yet, that is when we may offer them the enhanced version of FlyPi PCB.
[image]
Figure 1 - The concept of designated modules
Here, the main objective is to determine specific modules and modules that are to be implemented in the future. I mean the current version of FlyPi have a lot of things for research purposes. However, there should be some ideas that were omitted due to the lack of manpower or time (maybe both). 

To summarize:
1) What about this concept? The small set of specific purpose modules.
2) What about specific modules for FlyPi? Is it Peltier module or there is more?
3) What modules are needed and we can develop? I see it as the complex CAD/electronics issue and interesting task.  
4) If we are good to go, what can I start working with?

amchagas, 2019-11-07:
Hi @isobianin !

Thanks for putting time into thinking about this system. In principple I like the idea. One thing that is not entirely clear is what do you mean by "breakout system"? I mean, how does it differ from the specific purpose module, or from the controlled object?

In terms of controlled objects, here are some candidates for research in general:
- Servo motor (depending on size needs a dedicated power source, where the 5V output from arduino won't cut it)
- High power LEDs (dedicated power supply with high power resistor to regulate current?)
- Peltier element (h-bridge)
- transistor switches (kind of a "generic" system to turn things on/off)
- Simple Vcc, signal, ground  breakout
- temperature sensor
- humidity sensor
- gas sensor

I think this is could be generic and big enough to be transformed in a different project. This would be better for people who read the paper describing the Flypi, as they would still find this version which is somewhat similar to what is described in the paper, and better for us as it would allow us to develop without previous "prejudices" and constraints.

isobianin, 2019-11-07:
Hi @amchagas !
By the breakout system I mean some kind of main PCB (the hub perhaps?) which consists of the microcontroller and lots of ports. These ports are connected to specific modules, for example Peltier. Then the module is connected to things it is supposed to control. Of course, specific module may have controlled object on board (like sensors).

Speaking about modules, I will think this through as much as I can.

Totally agree on all points about the new project.

amchagas, 2019-11-11:
Hi @isobianin,
cool, I get it now. 
About the new project, would you like to setup a Github repository and invite me as a collaborator? 
If you are not that confortable with Github yet, I can also do this. Just let me know!

isobianin, 2019-11-14:
Hi @amchagas! Sorry for the delay, I created the new repository and invited you

closed 2021-05-27 by amchagas

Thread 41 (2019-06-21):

amchagas/Flypi #41: improve system to hold samples on manipulator

amchagas, 2019-06-21:
The current systen for holding samples only allows microscope slides to be held and it is based on a tight fit. If a thicker or thinner microscope slide is used, it is a bit troublesome for the user. 

To correct this, a system with a screw lock would be nice. Maybe re-using the printed screw system present in the other parts of the system. Another nice addition would be to have an interchangeable head, where different holders could be placed in, depending on what the user needs in terms of attachement.

Part that holds the microscope slide:
https://github.com/amchagas/Flypi/blob/master/3D_print_files/v2.0/STEPs/Manipulator_Zaxis.step

Here are the files containing the screw system (as guidance):
https://github.com/amchagas/Flypi/blob/master/3D_print_files/v2.0/STEPs/NeckTriangle_Thread.stp

https://github.com/amchagas/Flypi/blob/master/3D_print_files/v2.0/STEPs/NeckTriangle.stp

ODESSARAMBO, 2019-07-04:
Hello. I propose the next system that allows having changeable microscope slides. It functions as C-clamp and consists of 4 parts: screw, frame, top and bottom plates. Frame can be placed on either side and it is fixed in place by m3 screw (however, it can be mounted without them). The hole system uses the interchangeable system from the issue #40. Generally speaking, it is improved design that was included to the second job proposal.
[image]

isobianin, 2019-07-12:
Hello. I see that this issue has not been updated much. Here are step files of parts I mensioned here and in #40. Hope it will help you. Would really appreciate feedback so I know whether you will use or the problem is alredy solved.
Actually have some ideas on your next problems with enclosures. I can do it on voluntary terms but it will take longer time to complete
[holder.zip](https://github.com/amchagas/Flypi/files/3387192/holder.zip)

amchagas, 2019-07-15:
Hi! Thanks for sending this in. This issue hasn't been worked on yet. It looks nice, and I can find some time to print and test it tomorrow or the day after... 

I really appreciate your help!

isobianin, 2019-07-15:
Hi! Okay, got it. Looking forward for the prototyping phase

amchagas, 2019-07-22:
Hey,
I managed to print this out today, and some of the parts are too thin for the printer software to capture and properly slice it, so the parts end up printing "incomplete", for instance the m3 holes on the base do not print.
Also the top and the bottom plates do not slide in the zaxis base as the fit is too tight...

isobianin, 2019-07-22:
Hi. Could you please send me some photos of failed parts? Also would be nice to know the model of your printer. And about that m3 holes. What about the same m3 holes but made in the z-axis detail (#40)? Are they damaged (incomplete) too?

isobianin, 2019-07-22:
And about fit. Are those holes for nuts too tight in width or in height?

isobianin, 2019-07-23:
Hi @amchagas . In order to identify tolerances I propose to use the next set of parts that will help us to achieve our goal. In the archive you will find 5 parts that correspond to the questionable places in issues #40 and #41. Those are holes for nuts (#40) and T-connectors (#41). Moreover, from here and on it would be really good material-wise choice to print questionable parts of the main detail in order to define "printability"
[tolerances.zip](https://github.com/amchagas/Flypi/files/3421985/tolerances.zip)

amchagas, 2019-07-24:
Hi @isobianin 
The printer currently in use is a prusa mk3s https://www.techradar.com/uk/reviews/original-prusa-i3-mk3s

the holes for the nuts are fine (those are M4 nuts and bolts).

The fits that were too narrow only happened for the printed parts that had to slide onto each other. Below are photos of the parts. 

[image]
[image]

I can print the parts in the archive later today. As a reference, adding a 0.1 to 0.2mm tolerance for sliding parts has given us some ok results on previous projects.

isobianin, 2019-07-24:
Hi @amchagas. Thanks for photos and information about printer

isobianin, 2019-07-24:
About tight fit. I assumed that tolerance 0.2 mm would be enough (rule of thumb for most 3d printers) but, as the result shows, some things can only be solved by trial and error

isobianin, 2019-07-25:
Hey. Here is the connector from file Manipulator_Zaxis_base. Increased width of walls where the holes for m3 are
[base_connector.zip](https://github.com/amchagas/Flypi/files/3429769/base_connector.zip)

amchagas, 2019-07-29:
Hi, 
so the conclusion from printing the parts for test was that the smaller versions of both fits (m3 holes and t shpaed) are good. The bigger ones are too large I think.

second and fourth photos are the larger t shaped fit

[image]
[image]
[image]
[image]

isobianin, 2019-07-29:
Hi. I see. Will adjust design asap. I think we could go for tighter fit but we may aswell use this knowledge somewhere else

isobianin, 2019-07-30:
Here are corrected versions of z_axis, clamp base and clamp top. I forgot to mention but you have already printed parts where shaft and holes were changed. I mean, that you will reprint z_axis and base anyway, but the top part of clamp (where small cylindric detail is) may have to be reprinted. But I think that printed part should fit too, but it may be a little bit loose.
Also, I increased width on walls that connects base with pillar so now it should be printable.
[corrected.zip](https://github.com/amchagas/Flypi/files/3445621/corrected.zip)

isobianin, 2019-07-30:
I have made all necessary changes. Also I have increased width of walls that connect base with pillar. I forgot to mention but the hole T-system had slight dimension rework. You are going to reprint z_axis and base anyway but the top (with little cylindric detail) may have to be reprinted too. But I suppose that the current part will fit due to the tolerances but it may be a little loose 
[corrected.zip](https://github.com/amchagas/Flypi/files/3445673/corrected.zip)

amchagas, 2019-07-31:
Here are the printed parts: 
[image]
[image]
[image]

The fits seem alright for now, but the plates do not have enough space in between them. I mean the base of the zaxis has the negative t-shape, but it is not long enpough so that the plates are far a part enough, as can be seen in photo1. 

also the threaded part could be a bit longer (longer thread), and it would be great if the handles could start stright at the top (would make it easier to print it)

isobianin, 2019-07-31:
Hi. I see. How much longer do want the thread to be? About handles - definetly my fault, I thought about this when it had already been printed. And about the length of t-hole in z-axis, somehow it just slipped my mind. How thick will (aprox) the thickest microscope glass be? I will increase depth based on that.
And another question. So does the core tightening system work? I mean, does it tighten slides inbetween and does the ball on screw and its connector need any tolerance rework? Just to be sure so there will be less material loss.

isobianin, 2019-07-31:
Increased depth to 13 mm (pic.1)
[image]
Pic. 1 - New depth
Patched bolt handle and added +5mm to thread (before it was 15mm)

isobianin, 2019-07-31:
[changed.zip](https://github.com/amchagas/Flypi/files/3452827/changed.zip)

isobianin, 2019-07-31:
So now it can hold slides up to 3 mm in thickness without moving out of bounds

amchagas, 2019-08-09:
Also printed these guys and it is looking good. however the top plate doesn't slide down when the screw is turned. What ends up happening is that the top plate bends downwards when enough turns are made on the screw. In the last image it looks like this is causing strain on the other joints. 

I wonder if a system where both plates were fixed (with 4 mm distance or so) and a printed screw could go trhought the top plate would be enough? a little bit like the clamping system used for the other movable parts?

[image]
[image]
[image]
[image]

isobianin, 2019-08-09:
Ok, I will send here some sketches that illustrates your proposed design as I understand it. Also I was thinking about this issue after completion of the last one #45. I will attach sketch of my idea too

isobianin, 2019-08-09:
So here is the finished simple system that I actually proposed as the second variant during the time we started this project. Also, reduced material usage by creating gaps in details. Picture 1 has annotations in it that explains assembly.
[image]
Pic. 1 - Simple M3 thread system
Attaching step files so you can test it right away
[holder m3.zip](https://github.com/amchagas/Flypi/files/3486518/holder.m3.zip)

isobianin, 2019-08-09:
How I see your technical proposal (pic. 1)
[image]
Pic. 1 - Technical proposal

amchagas, 2019-08-09:
So the drawing is what I'm thinking about, yes. 
I can print the other holder as well to compare

isobianin, 2019-08-09:
So here I made your variant (pic. 1 and pic.2) and combined version (pic. 3). Fixed position variant has 4 mm clearence.
[image]
Pic. 1 - Variant with fixed position
[image]
Pic. 2 - Slice of model
[image]
Pic. 3 - Top plate with threaded hole and wings for M3 screws
And bolt for tightening slides (pic.4). Has 20 mm thread legth
[image]
Pic. 4 - Bolt (handle from #45)
[holder fixed.zip](https://github.com/amchagas/Flypi/files/3488066/holder.fixed.zip)

amchagas, 2019-08-14:
Hi, 

this looks quite nice too!
I'll try to pop itin the printer today!

isobianin, 2019-08-14:
Hello. Ok, looking forward to seeing it. Just to be sure (because this issue has a lot of things) there is a zip named holder m3.zip and holder fixed.zip. Totally there are 3 variants of the same thing but the last archive (holder fixed.zip) is like definiteve edition where all things can be tested:
- nut holding
- applying pressure via bolt
- combined version with both methods

amchagas, 2019-08-14:
cool, thanks!

amchagas, 2019-08-14:
also, I had already printed the other clamping solution, but the nut pockets were too big.
[image]

isobianin, 2019-08-14:
Yeah, I see it. I suppose it still can function as a test object. Those tolerances are taken from holes that we were testing in order to find the right sizing. I will look up my files, maybe something went wrong or we can make holes smaller

isobianin, 2019-08-14:
Those are nuts for m4 thread, sorry. Somehow, mixed it all up. So holes are probably too tight for m4 screws. I will make them proper diameter. I think, that it is better to stick with m4 nuts because they are a bit bigger than m3 and so less likely to have issues with size distribution (mainly 3d printer prints sizes differently every time and smaller we go, more precise equipment is needed)

isobianin, 2019-08-14:
Basically, it is previous archive but with m4 holes
[holder m4.zip](https://github.com/amchagas/Flypi/files/3500910/holder.m4.zip)

amchagas, 2019-08-15:
I think we have a winner here. Below are the photos of the fixed system with only one printed screw. It holds well, even if the part is quite large and "heavy"

[image]
[image]

If you are ok with this, I would use this design and call this issue and the other one related to Z axis stability closed?

isobianin, 2019-08-15:
Good job! Sometimes less is more. Just the right thing for current issue

amchagas, 2019-08-16:
cool, do you want to make a pull request with this final version so that your name can be added to the contributors list and we can close this and the other related issue?

isobianin, 2019-08-16:
Hi. So how exactly can it be done? I just cannot find the button

amchagas, 2019-08-16:
I see you created a fork of this project, so the best way to create a pull request would be to follow these guidelines: https://help.github.com/en/articles/creating-a-pull-request-from-a-fork

isobianin, 2019-08-19:
Hi @amchagas ! So I have uploaded all files that we have designed together. As I understand this, I will create pull request when we have design in #43, #44 and #45 settled. I created folder with my surname in /STEP files folder to keep things organized.
P.s. Aforementioned issues have been updated. Just waiting for approval

amchagas, 2019-08-21:
Hey @isobianin, yes, you are completely right! 
I'm printing the updated versions and can let you know when I'm done.

isobianin, 2019-08-21:
Hi! Okay, I get it with pull requests, thanks.
Looking forward to seeing print results

isobianin, 2019-08-26:
Hi! What is the situation with the details? Is everything alright?

amchagas, 2019-08-26:
Hi!
so the base is printing nicely. The pcb case cover and the system to hold petri dishes I documented here https://www.dropbox.com/sh/418cd881mosbbwr/AABIq8Ff3xSaW14b0SKrVxpJa?dl=0

isobianin, 2019-08-26:
Okay, I see. So there is a small tolerance problem with pcb case. Strange, was it there when you have printed it last time? I will make adjustments in model. I hope that it is still usable or is it so bad that you cannot open it?
Speaking about holder, I see that there is a backlash. Is it present in other places where the same srcew system is used? And what about other parts of the holder. Have you tried assembling it? Just want to know whether the whole system is working.
Please, correct me if I have missed something.
P.s. Is there a way to contact you via email? I would like to discuss same matters if it is possible

amchagas, 2019-08-26:
Hi, 
This is still usable! don't worry. yeah, I don't know if we didn't notice that little thing because before it was getting stuck in the inner thinner part. 

I don't see that much backlash on the other parts the screw system is being used, but then again the screws are shorter, and have other purpose. The other thing I can comment is that the rectangular slides are ok, but a bit on the thin/"too delicate" side, also they tend to slide out of the rails a bit (maybe a "V" system would do better?). As far as I remember the other parts were fine, and they fit nicely when assembled as a whole. 

you can always send me a message @ andremaia.chagas[at]gmail.com! but keep in mind this potentially keeps other people out of this discussion thread. 

Once again, thanks for all the help with this project!! really appreciated! 

You can send me an emai

amchagas, 2019-09-11:
Solved by @isobianin contribution via PR https://github.com/amchagas/Flypi/commit/50d048502420fd8981893c8c185ba7404e968846

closed 2019-09-11 by amchagas

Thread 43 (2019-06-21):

amchagas/Flypi #43: acessing cables without unmounting the boxes

amchagas, 2019-06-21:
In order to plug and unplug modules, users need to disassemble at least the PCB box. 
What we want is to create a click on or flipping system where the modules can be plugged and unplugged in an easier manner. 

Here are the files for the PCB box, where the modules are plugged in and out:

https://github.com/amchagas/Flypi/blob/master/3D_print_files/v2.0/STEPs/PCBCase_Top.stp

https://github.com/amchagas/Flypi/blob/master/3D_print_files/v2.0/STEPs/PCBCase_Bot.stp

isobianin, 2019-07-20:
Does the highlighted hole serve functional purpose? What exactly it does?
[image]

isobianin, 2019-07-20:
I have in mind a pair of hinges that will be placed either there or where the hooks currently are. I thought that this side of enclosure is less likely to be loaded with ports but I do not know the used PCB layout

amchagas, 2019-07-22:
Hi, sorry it took me a moment to take a photo of the case with the cables and a part of the pcb.

[image]
[image]

isobianin, 2019-07-22:
Thanks for the photo! It is quite informative! However, I still have questions. Is the opposite side of the box (pcb) loaded with cables or ports too? I don’t see it in this photos, but structure of the enclosure have holes for ports there.
It is important for the hinge system I want to implement

<sub>Sent with <a href="http://githawk.com">GitHawk</a></sub>

isobianin, 2019-07-22:
Yeah, I see that both sides are loaded

<sub>Sent with <a href="http://githawk.com">GitHawk</a></sub>

isobianin, 2019-07-29:
Hello @amchagas . I am almost finished with the new design. For now a test for hinges is needed 
[hinge_test.zip](https://github.com/amchagas/Flypi/files/3442756/hinge_test.zip)

amchagas, 2019-07-29:
hi @isobianin, great, thanks! can print these tomorrow

isobianin, 2019-07-29:
So this is what I came up with. The first picture demonstrates hinges placement
[image]
The second one illustrates clicking system from this same enclosure with stifeners (as in #42)
[image]
In the third picture you can see how the case looks being open
[image]
Attaching step files in case printing phase goes well and hinges fit.
[PCB_mod.zip](https://github.com/amchagas/Flypi/files/3443610/PCB_mod.zip)

amchagas, 2019-08-09:
Hey!
so I managed to print this, and there is one main issue, namely that the tabs in the bottom part are too thin and they broke right off in the first opening of the system... I wonder if making them thicker would be too much trouble?
[image]

isobianin, 2019-08-09:
Hi. Okay, I will correct strength of the detail. Shame that this occurred on the printed parts

isobianin, 2019-08-10:
Increased thickness of wall towards hull (pic. 1)
[image]
Pic. 1 Thickness
[PCBCase_Bot_mod_v2.zip](https://github.com/amchagas/Flypi/files/3488750/PCBCase_Bot_mod_v2.zip)

isobianin, 2019-08-11:
Created another variant of hinges that are more stable, however, they take a bit more place in the interior (pic.1-pic.4)
[image]
Pic. 1 - Bottom
[image]
Pic. 2 - Top (outside view)
[image]
Pic. 3 - Top (inside view)
[image]
Pic. 4 - Assembled
[image]
Pic. 5 - Opened
[PCB_case_alternate.zip](https://github.com/amchagas/Flypi/files/3490288/PCB_case_alternate.zip)

amchagas, 2019-08-15:
Hi! so here is the new version printed. 
It looks quite nice and the hinges do not break :) 

[image]
[image]

amchagas, 2019-08-15:
I think we are ready to call this one closed?

isobianin, 2019-08-15:
Here is patched version (pic. 1)
[image]
Pic. 1 - Short version
Actually, having step file with pcb layout would have been nice, but are almost finished with this one
[pcb_case_short.zip](https://github.com/amchagas/Flypi/files/3505270/pcb_case_short.zip)

isobianin, 2019-08-28:
Adjusted tolerances based on the latest (26.08.2019) prototype
[PCBCase_Bot_v2.zip](https://github.com/amchagas/Flypi/files/3550609/PCBCase_Bot_v2.zip)

amchagas, 2019-09-11:
Solved by @isobianin contribution via PR https://github.com/amchagas/Flypi/commit/50d048502420fd8981893c8c185ba7404e968846

closed 2019-09-11 by amchagas

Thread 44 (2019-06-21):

amchagas/Flypi #44: base optimizations

amchagas, 2019-06-21:
The base could use some optimizations:

1 - Currently it takes quite a while to print, it would be useful to hollow out some parts so that it prints faster. It should be kept in mind that hollow parts require some sort of support/bridge to print properly.

2 - on the top side of the base, where the peltier cables go in, one of the sides is higher then the other. we want to fix that by making both sides as low as the current lowest side and to make the slits curved and not squared as they are currently (this will lead to better finishing when it is printed)

amchagas, 2019-06-21:
https://github.com/amchagas/Flypi/blob/master/3D_print_files/v2.0/STEPs/Base.stp

isobianin, 2019-07-21:
Want

isobianin, 2019-07-21:
Here I have multiple questions:
1. Is this an orientation for the printing?
[image]
2. What are the functional purpose of all holes and how does this part connects to the others? Some triangular holes are blocked (picture below). Need to know more because I want to create holes as shown in the picture.
[image]
3. Have a problem with the second point of this issue. Do the circled points show the slits for peltier cables (picture below)? At least, I think so. In this case, there is now difference in height between slits (pink lines in the picture)
[image]

amchagas, 2019-07-22:
hi @isobianin ,
to answer your questions:
1 yes, the base is printed upside down, as you show in 1.

2. the triangular holes are used as fits for the necks (https://github.com/amchagas/Flypi/blob/master/3D_print_files/v2.0/STLs/Neck_L.stl). The pieces "blocking" the necks are not actually blocking this fit, and they are there to hold a fan in place (placed from below to be sitting under the peltier element).

3 yes, this part of the issue was resolved already.. sorry for not updating the description.

isobianin, 2019-07-22:
Hi @amchagas , thanks for information. But the slits are still need to be curved, right?

amchagas, 2019-07-22:
You mean so that the cables fit in them? I think it is not that pressing, since squared slits are working fine too..

isobianin, 2019-07-22:
Okay, leaving it squared

isobianin, 2019-07-31:
Hi @amchagas . Here is an update on this issue. Picture one shows amount of material before.
[image]
Pic. 1 - Slice of model (before)
The next one - after rework.
[image]
Pic. 2 - Slice of model (after)
[image]
Pic. 3 - Light version of the base
For example, numeracly it can be shown as following:
V = 62330.061064 mm3 (before)
V = 22574.223411 mm3 (after)
Almost 3 times lighter. 
Attaching file to this comment and waiting for your approval of this design
[Base_light.zip](https://github.com/amchagas/Flypi/files/3450480/Base_light.zip)

amchagas, 2019-08-14:
Hi, 
So I managed to print this and indeed it cut the printing time in half!
There is one issue though that the most inner wall is too thin and breaks easily... would it be hard to increase the wall thickness a bit, or add reinforces along the wall? (as long as it doesn't cover the triangular holes?
[image]
)

isobianin, 2019-08-14:
Okay, I will make necessary adjustments

isobianin, 2019-08-14:
I have looked up my model. So is there a problem in all other walls too? Because they are all the same and have 1.5 mm thickness

amchagas, 2019-08-16:
I think the problem is mostly with the inner ones... maybe the bridges and other elements closer to the outter walls somehow make them stiffer?
Or maybe there is an issue with the slicing software, but then this is something that is not easy to change from our side...

isobianin, 2019-08-16:
Hey. Increased thickness of inner walls by 1 mm. (pic. 1, pic. 2)
[image]
Pic. 1 Reinforced model
[image]
Pic. 2 Interior
[base_light_reinforced.zip](https://github.com/amchagas/Flypi/files/3509923/base_light_reinforced.zip)

amchagas, 2019-09-11:
Solved by @isobianin contribution via PR https://github.com/amchagas/Flypi/commit/50d048502420fd8981893c8c185ba7404e968846

closed 2019-09-11 by amchagas

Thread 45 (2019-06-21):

amchagas/Flypi #45: Holder for petri dishes

amchagas, 2019-06-21:
The current petri dish holders are fixed to two different sizes. It would be nice to have a clamping system that is able to handle dishes and other containers with different sizes. 
It can use the thread/screw system already implemented on the system.

here are the files for the petri dish holders:
https://github.com/amchagas/Flypi/blob/master/3D_print_files/v2.0/STEPs/PetriDish_56mm.STEP

https://github.com/amchagas/Flypi/blob/master/3D_print_files/v2.0/STEPs/PetriDish_36mm.STEP

and the thread/screw system:
https://github.com/amchagas/Flypi/blob/master/3D_print_files/v2.0/STEPs/NeckTriangle_Thread.stp

https://github.com/amchagas/Flypi/blob/master/3D_print_files/v2.0/STEPs/NeckTriangle.stp

isobianin, 2019-08-06:
Hi @amchagas ! Are there any news about previous issues? I have been working on this since then and have some things to show.
There are two variants of the vise that supposed to replace old holding system. First variant uses stift to hold the movable bolt in place and consists of movable and immovable jaw placed on rails, bolt with the thread (the one you already have in your project) and dubels to hold cylindric and other forms with diameter up to 70 mm (pic. 1).
[image]
Pic. 1 - Vise with stift
The slice of this model is shown below (pic. 2).
[image]
Pic. 2 - Slice of the vise with stift
The problem here that bolt is held by only stift. So there is another variant that has longer bolt so the structure can be disassembled (pic. 3).
[image]
Pic. 3 - Vise with prolonged bolt
The next slice illustrates how bolt is stopped.
[image]
Pic. 4 - Slice of the vise with prolonged bolt
Movable jaw looks like this (pic.5)
[image]
Pic. 5 - Movable jaw
So this variant is arguably more durable and secure but may come undone when used in its maximum holding position (diameter more than 70 mm) (pic. 6)
[image]
Pic. 6 - Disassembled vise with prolonged bolt
For reference, I have place 56 mm holder in this system (pic. 7)
[image]
Pic. 7 - Reference assembly

isobianin, 2019-08-06:
[vise.zip](https://github.com/amchagas/Flypi/files/3472472/vise.zip)
There is note in this archive in order to assemble chosen vise correcrtly without printing unnecessary parts

amchagas, 2019-08-07:
Hi @isobianin !
this looks quite nice! Thanks for taking the time to develop it :) I had some time problems last week and the printer also acted out... So I'm still printing the other parts and can pop this in when those are done.

isobianin, 2019-08-07:
Hi! Ok, looking forward to seeing the results of the latest prototypes

amchagas, 2019-08-14:
I printed this one as well, and there was an issue with the sliding T parts... sorry!

Namely they don't print so well without support, I wonder if having them as V shaped would be too complicated? this would facilitate printing and possibly making sliding easier...

isobianin, 2019-08-14:
Got it

isobianin, 2019-08-14:
Changed rail profile so now it is just simple rectanle (the safest of all options) (pic. 1)
[image]
Pic. 1 - New profile
[vise_v2.zip](https://github.com/amchagas/Flypi/files/3501053/vise_v2.zip)

isobianin, 2019-08-28:
Deacreased tolerance in the immovable jaw nut (pic. 1 and pic. 2). 
[image]
Pic. 1 - Before
[image]
Pic. 2 - After
File to test this tolerance here:
[nut_test.zip](https://github.com/amchagas/Flypi/files/3550808/nut_test.zip)

isobianin, 2019-08-29:
V-shape rails added (pic. 1)
[image]
Pic. 1 - V-shape rail
There was a problem with the rails that I have been thinking. What bothered me is that they just hanged in space. I added support in the movable jaw, but now jaws have some offset (pic. 2). 
[image]
Pic. 2 - Sizing
Files to print if previous tolerance test goes well
[vise v3.zip](https://github.com/amchagas/Flypi/files/3554162/vise.v3.zip)

isobianin, 2019-08-29:
I have designed another variant of the vise. In this system rails are now printed separately and then mounted in the immovable jaw (pic. 1 and pic. 2)
[image]
Pic. 1 - Front
[image]
Pic. 2 - Back
Rails have slots for screwdriver just in case. This vise does not have any offsets but it is now 5 mm higher
[vise_screws.zip](https://github.com/amchagas/Flypi/files/3556639/vise_screws.zip)

isobianin, 2019-09-03:
Hi @amchagas ! What about models? Is everything good?
Also, I have a question. If our designes are used by other researchers via 3d printing, is there a necessity of creating assembly instructions? I mean, just a set of pictures with parts' names and maybe some sequences of actions. Basically, pictures that I send when design is finished but with the latest versions of each part

amchagas, 2019-09-04:
Hi @isobianin things look good!
the round screwable rails are definetly a nice way to do things! below are some photos. I think the only commentary I have is that the lock system for the screw is a bit too thin for 3D printing, I broke one trying to plug it in and out...  (see first image to know which part I mean)
Creating instructions for the system would be nice add on, if it is really just the pictures you sent.. otherwise I wouldn't want to you to have the extra trouble.
[image]
[image]

amchagas, 2019-09-04:
I think this one can be closed if you don't have more time to work on it, as this last iteration is quite good!

isobianin, 2019-09-04:
I am happy that this device works as intended. Thank you for appreciating the time I spend. I just want to make sure that every system that was designed or modified during this period is done as best as I can do it. I will make instructions soon just to wrap everything up nicely. For me this kind of work is just too interesting
A new bolt needs to be tested (pic. 1). The trick here is to identify whether it will print such overhanging structure (I do not see a problem here because we have already done it with smaller diametres but who knows what may happen)
[image]
Pic. 1 - Bolt lock system
It is just a regular bolt that is missing a handle and shortened to the minimum. Movable jaw included just to test tolerances (pic. 2)
[image]
Pic. 2 - Movable jaw part for test
[lock_test.zip](https://github.com/amchagas/Flypi/files/3575685/lock_test.zip)
Archive if test is good
[vise_screws_v2.zip](https://github.com/amchagas/Flypi/files/3575703/vise_screws_v2.zip)

isobianin, 2019-09-05:
Structure (pic. 1) and instructions for assembly (pic. 2). If something is wrong or written unclearly, please tell and I will correct it. Small changes will not take much time. Also, pictures may have some mistakes in their texts so please tell me if you find any. 
[image]
Pic. 1 Structure
[image]
Pic. 2 Assembly
P.s. I see that this device is the only one that actually needs some kind of clarification (microscope slides holder has only two parts, pcb enclosures too). But I may be wrong

amchagas, 2019-09-09:
Hi @isobianin , 
the instructions look great! thanks for putting them together. 

The test part printed also printed well! 

I think this closes all the issues? or did we still have something to check/change?
If they are all done, I would ask you to make a pull request with the latest files and we close the issues once the PR is made.

isobianin, 2019-09-09:
Hi! Okay, good job! I will double check files just in case, look into issues one more time and than make a pull request. It will be a matter of one or two days

amchagas, 2019-09-11:
Solved by @isobianin contribution via PR https://github.com/amchagas/Flypi/commit/50d048502420fd8981893c8c185ba7404e968846

closed 2019-09-11 by amchagas

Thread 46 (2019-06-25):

amchagas/Flypi #46: Servo motor & the 2nd version of 3D printed LED matrix holder

LabuserTu, 2019-06-25:
Hi, first thanks for the detailed instructions for such a cool microscope! We´ve managed to build one, using the PCB version 0.6  and the 2nd version of 3D-printed parts (some photos attached). It works as expected - a manual, together with some forum discussions were helpful enough to make the basic system running. Still, we have some extra questions and would be grateful for your opinion. The prometheus science forum seems like a better place to open this issue but I was somehow unable to register neither normally nor via Twitter. 

We´ve implemented the automated focusing of the RaspPi Camera but it seems, with the printed cogwheels provided, that it can´t really do it´s job? Servo´s limited 180 degrees of rotation covers only a small range of the lens´ thread which enables focus adjustment. Since the cogwheels are quite tightly attached to each other, it is also not possible to roughly adjust the focus manually, at the same time the cogwheels are attached. Have you also encountered this issue or is there a better way to construct the automatic focusing? We´re using Reely Analog Servo S-0009 MG. Besides increasing the cogwheel size, we were thinking a bi-directional DC motor could help us with the issues. Maybe something similar as it is described here:  https://learn.adafruit.com/adafruit-dc-and-stepper-motor-hat-for-raspberry-pi/overview ? Or is there a specific reason the servo motors are used? Any suggestion would be appreciated. 

Also, as it seems servo motor cogwheels and the LED matrix holder STL files are missing in the second version. Maxime kindly sent the cogwheel STL files. As for the holder, I´ve read that you haven´t update it due to lack of public interest. Just in case, I wanted to ask, wheather it has been created in the meantime?

Lastly, it´s not really crucial but we have a problem with the zap function in the LED1 module. It works well for the LED Ring but nothing happens when the zap button is pressed to control the timing of  high-power UV LED. I´ve seen that the arduino sketch (flypi_development.ino) in the LED1 section doesn´t include similar zap parts as in the LED Ring section - is this why it doesn´t work and should still be added?

Thank you very much!

[image]
[image]
[image]
[image]
[image]

amchagas, 2019-07-01:
Hello, 
great that you are building one of these :)

Yes, it would be great to have this conversation in the forum so that we keep all issues related to usability and problems during build in one place. I took a look at the forum and it seems a recent update on the database broke the signing up system. Could you try it again and let me know how it goes? www.forum.prometheus-science.com
Thanks!

LabuserTu, 2019-07-03:
Hi.

thanks for the reply.
It worked, I registered and created a new discussion there.

Best,
Nina

amchagas, 2019-07-04:
This has moved to a thread in the FlyPi user forum: https://www.forum.prometheus-science.com/index.php?p=/discussion/615/servo-motor-the-2nd-version-of-3d-printed-led-matrix-holder#latest

closed 2019-07-04 by amchagas

amchagas, 2019-10-23:
Hi @LabuserTu please take a look at this thread: https://github.com/amchagas/Flypi/issues/47
@isobianin has worked on a holder for the matrix!

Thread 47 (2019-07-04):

amchagas/Flypi #47: Create a matrix holder for version 2 of the printed parts

amchagas, 2019-07-04:
It seems more people than we thought are using the LED matrix that was published with the paper. Since there wasn't much use from our side, we didn't port the holder of version 1 to version 2 of the printed parts. 

We want to create a holder for it. The matrix is this one: https://www.adafruit.com/product/870

isobianin, 2019-09-17:
Hello @amchagas ! It is this and #34 issues I have referenced in the email. Actually, I am writing this because I have not yet recieved any form of notification from you that my letter had been read or at least seen. More than sure that it is either in "spam" folder or it is lost somewhere in other emails. The subject is "Summary of the work done and further cooperation". 
Regarding this issue, how holder is mounted on the microscope. Or is it a standalone object? What are files for previous model?

amchagas, 2019-09-17:
Hi @isobianin ! 
Just replied to your email. Sorry for the delay!

The matrix is the one mentioned on my comment above here, and the holder is this one https://github.com/amchagas/Flypi/blob/master/3D_print_files/v1.0/individual_stls/matrix.stl (there is also an STEP version on the same folder).

The holder should work similar to the camera or ring holder of the current printed version, so something that can slide up and down the "necks" and that can be locked in place with a printed screw.

isobianin, 2019-09-18:
Hi! Okay, I will look into these files and see what I can do. Possibly, there will be more questions to come. 
Also, what about heat dissipation? Is everything alright with it? This question bothers me because of 2 things:
1) I have been browsing through files one day and have found file named something like "heat dissipator for LED". Probably, there was or there is a problem with that. And this ties to the second thing;
2) Surprisingly, in my diploma project I am developing methodic for designing LED radiators with a help of open source software. At least, we have a chance to simulate this matrix if such necessity exists.

isobianin, 2019-09-19:
Hi @amchagas. So here are more questions (fig. 1).
[image]
Fig. 1 - Questions
1) What is the purpose of this hole (red circle)?
2) How exactly is matrix held in place? I thought that this holder would have some kind of sufrace it can lay on. At least I wanted to implement it in a new version because I see that this design is quite unstable for LED. Or can it be that the matrix is simply placed on top of rectangular hole?
3) There is a certain distance between the centre of rectangular hole and the centre of the neck. Is it critical or it may differ in the new version? I say that it may differ up to 10mm

isobianin, 2019-09-20:
I have designed two variants (fig. 1, 2)
[image]
Fig. 1 - LED holder
[image]
Fig. 2 - Alternative version (file name LED_holder_rectangle)
During the design I had some troubles with dimensions that are mensioned on the developer website so I took all the necessary data from PCB layout files. Assembly check (fig. 3)
[image]
Fig. 3 - Checking assembly
[LED holders.zip](https://github.com/amchagas/Flypi/files/3634483/LED.holders.zip)

amchagas, 2019-09-23:
Hi @isobianin !
Some answers:
The heat dissipators are only needed for a high powered led we are using for fluorescence imaging, but this is already covered with this [part/mount]() where the heat dissipator is glued to the led and the whole thing is fitted into the printed part. 

This Matrix doesn't heat up enough to be a concern.

1 - On fig1, it is indeed that hole is for cables. That can be better implemented though, as in the current state, one will need to unplug the cables from the board if the holder needs to be exchanged (in case it breaks, etc). 

2 - the distance of the center of the matrix to the center of the neck hole is based on two things: a) on the center of the camera when placed in its holder (LED matrix center and camera lens should be aligned), b) the matrix itself is connected to something adafruit calls a "backpack" which is a pcb board that is extending on at least one axis beyond the border of the matrix itself.

3 - The matrix is held in place by using the fact that the backpack behind the matrix is longer than the matrix itself, and a little bit of a tight fit around the matrix, so that the whole assembly can be turned in any position. 

I can print these out today and see how they fit with the matrix.

Thanks for putting this together!!!

isobianin, 2019-09-23:
Hi! Thanks for clarification. Luckily, I have guessed most of the answers.  Hope that prototypes will be alright.

isobianin, 2019-09-27:
Hi @amchagas ! Is there any update on this issue? And what about #34? I have left my commentary and thoughts there too

amchagas, 2019-09-30:
Hi @isobianin ,
sorry for the delay again. 
seems there was a problem with the scale of the matrix holder (see below
[image]
)

isobianin, 2019-10-01:
Hi Andre! That is odd. I can make necessary adjustments very quickly. However, you are showing me different matrix than the one mentioned in issue. Your post mentions a holder for https://www.adafruit.com/product/870 If we go to the website, we see the following (fig. 1)
[image]
Fig. 1 Adafruit Mini 8x8 LED Matrix w/I2C Backpack
Backpack dimensions are mentioned later as 20mm x 28mm x 4mm / 0.8" x 1.1" x 0.2"
Here it is as the footprint (fig. 2)
[image]
Fig. 2 - Footprint
So I made this holder for this matrix. 
I suppose, that matrix in your photo is this one https://www.adafruit.com/product/902 (due to the rectangular led-s)? (fig. 3)
[image]
Fig. 3 - New matrix
And its footprint is this? (fig. 4)
[image]
Fig. 4 - New footprint
So should I adjust holder (I will save both variants of previous matrix and the new one)? Is the new information about matrix accurate?

isobianin, 2019-10-01:
So I have made adjustments with an assumption that we are using this https://www.adafruit.com/product/902 bi-color LED.
Checked assembly in CAD (fig. 1).
[image]
Fig. 1 - Assembly check
[LED_holder_bi_color.zip](https://github.com/amchagas/Flypi/files/3677651/LED_holder_bi_color.zip)

amchagas, 2019-10-02:
Hi @isobianin ,
so sorry, I obviously linked the wrong board!
Thanks for updating the part, I'll print it here in a couple of hours and let you know

isobianin, 2019-10-02:
Hi, @amchagas ! Okay, looking forward to seeing the results

amchagas, 2019-10-02:
The matrix fits and the screw holes are aligned, so one can certainly fix it to the plastic holder that way. There is a small gap between the matrix and the printed part (last photo)
[image]
[image]
[image]
[image]
[image]

isobianin, 2019-10-02:
Here is an interesting thing. I have corrected dimensions and made new design for monochromatic LED. The thing is that the length between centers of mounting holes is shared between bi- and mono- LED. Thus, it makes already printed holder universal. However, I do not know why there is a gap, especially with given circumstances. Could it be that this particular matrix has some kind of offset?

Here are files for monochromatic LED but aforementioned dimensions render these files almost useless. Please, tell me whether I should download them to repository or the previous pack of holders is enough.
[LED_holder_mono_color.zip](https://github.com/amchagas/Flypi/files/3682974/LED_holder_mono_color.zip)

amchagas, 2019-10-03:
Hi! 
I'm really sorry about not noticing the difference between the monochrome and the bicolor versions. I thought the backpack would be the same for them. 

the issue could also be that the Matrix I have here is at least 3 years old, maybe they've updated components.

I think I'm happy with the pack already made, since it can be used for both matrices? So if you are also happy with it, send them to the repo. Other than that I can print the last version you made and see what it looks like.

isobianin, 2019-10-03:
Hello @amchagas !
I am glad that we put effort into finding out the cause of disinformation. Now I have one more thing to add. I am sorry but today is the day when I have finally understood what problem with cables you have referenced in one of your previous posts. This means that I prepared one more version of holder. It is a dead simple concept but I think it will be enough to solve this subissue efficiently (fig. 1).
[image]
Fig. 1 - Cave design
This new cave that is 13 mm long is supposed to be used as an excess room. This room allows LED to be taken out (measured with the highest matrix). Seems that this design is quite good but cables may be touching PCB (backpack). I mean I am being picky here but, still, it is what we are going to end up with. It looks like these cables will not interfere with LED ability to work especially with given PCB layout.
LED needs to be uplifted and rotated in order to be taken out (fig. 2)
[image]
Fig. 2 - LED position for disassembly
Yes, the cave may be mirrored to the other side of holder. But I want this design to remain somewhat rigid and do not want to weak support structures more than they need to be.
[LED_holder_universal.zip](https://github.com/amchagas/Flypi/files/3686673/LED_holder_universal.zip)

amchagas, 2019-10-07:
Hi @isobianin 
thanks for preparing these. 
I'm printing them out now, will let you know how they turn out.

isobianin, 2019-10-07:
Hi! Okay, looking forward to it

amchagas, 2019-10-08:
Hey @isobianin this looks pretty nice! I think we can close this one too.

thanks a lot!

[image]
[image]

amchagas, 2019-10-08:
There is some "brim" from the print that I forgot to remove..

isobianin, 2019-10-08:
Hi @amchagas ! Indeed, things seem to be alright. Have you tested whether it can be disassembled without getting cables out from LED (it is still bothers me)?

closed 2019-10-23 by amchagas

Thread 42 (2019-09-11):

### ISSUE TITLE
Boxes closing system breaks

### ISSUE THREAD

**Issue by amchagas** [amchagas/Flypi#42]
The system to keep the boxes closed is too fragile, as the stress points are in the same axis as the printed parts. it would be great to develop a new closing/clicking system for the boxes where the locking parts do not break so easily. 

Here are the files for the boxes:
Raspberry pi case
https://github.com/amchagas/Flypi/blob/master/3D_print_files/v2.0/STEPs/RaspberryCase_Top.stp

https://github.com/amchagas/Flypi/blob/master/3D_print_files/v2.0/STEPs/RaspberryCase_Rails.stp

https://github.com/amchagas/Flypi/blob/master/3D_print_files/v2.0/STEPs/RaspberryCase_Bot.stp

PCB case:

https://github.com/amchagas/Flypi/blob/master/3D_print_files/v2.0/STEPs/PCBCase_Top.stp

https://github.com/amchagas/Flypi/blob/master/3D_print_files/v2.0/STEPs/PCBCase_Bot.stp

**Comment by isobianin** [comment]
Hello. In the Raspberry case I have added stiffeners along the exterior of hull. The bottom part remains unchanged and so there is no need in reprinting. 
![raspberry_top](https://user-images.githubusercontent.com/52375129/61581698-2f2d8800-ab2a-11e9-80e1-4f5d8fc5ec5b.jpg)
Do you need an analogous improvement in PCB case as it is in these repository or the end result must only meet criterias defined in #43? 
[RaspberryCase_Top.zip](https://github.com/amchagas/Flypi/files/3413827/RaspberryCase_Top.zip)

**Comment by amchagas** [comment]
Hi!

thjanks for this, Il try to print it today and let you know how it went. In principle we also need something like this for the PCB case...

**Comment by amchagas** [comment]
hi, 
So this worked quite well! The snaps are much more resistant now, but still flexible enough that they click on the bottom part of the board!

**Comment by amchagas** [comment]
Solved by @isobianin contribution via PR https://github.com/amchagas/Flypi/commit/50d048502420fd8981893c8c185ba7404e968846

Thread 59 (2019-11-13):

amchagas/Flypi #59: scroll bar

AndresGarelli, 2019-11-13:
Hi,

is it possible to add a scrollbar to the main window? Depending on the screen resolution, the main windows sometimes does not fit in the screen and some buttons are not accesible. I tried increasing the resolution in the Raspberry pi, but for an unknown reason, VNC does not show the desktop if it put in the highest possible resolution
thanks

amchagas, 2019-11-17:
Hi @AndresGarelli ,
thanks for reaching out and we are glad to hear people are using the Flypi,
I've started looking into this and should have a bit more time during the next days... Hopefully it is an easy fix.

amchagas, 2020-10-01:
@isobianin This is one of the issues I mentioned earlier. But let's talk about it once more before deciding on how to tackle it.

isobianin, 2020-10-01:
Hi @amchagas , I see it. My main question is whether there is a distinctive point from which we can start working. What I mean is that I am not that qualified yet in this area to see a clear solution or even a plan how to tackle it. I believe, as you mentioned in the previous reply here, it should not be that difficult. I know that for web pages there are means to automatically scale web page interface, or GUI in our case, so at least the general solution algorithm should be related to that in some way or another. If there are already some notes, I would be happy to look into them

amchagas, 2020-10-02:
Currently the GUI is written in PyQT5, using QTcreator. There area a couple of threads on Forums showing how to implement something similar such as [this](https://www.learnpyqt.com/courses/adanced-ui-features/qscrollarea/) and [This] (https://www.programcreek.com/python/example/108074/PyQt5.QtWidgets.QScrollBar)

Another solution which I think is a bit of an overkill (at least for me without much experience with Html, css, JS etc) would be to redo the GUI code using technologies that make use of the browser. [Python dash](https://plotly.com/dash/) I think would be a good candidate for this solution since it has a large community backing it, and it keeps the code in Python/.

I think it would be easier to simply add scrollbars to the current GUI.

isobianin, 2020-10-05:
Hi @amchagas ! This seems like a good point to start. And I agree with you that we should incrementally upgrade it to the desired variant. But it would be wise to begin it with the srcollbar.

I will look into it and post new information here

isobianin, 2020-10-10:
Hi @amchagas !
I have been looking into pyqt5 since we last discussed this problem. To begin, I have this window
[image]
Fig. 1 - Main window
I guess that I encountered some compatibility issues with widgets being a bit cut off. But the question here is whether a scroll bar should be added to all submenus(?) and should it be both vertical and horizontal? At least, I think that this issue may be resolved this way or maybe by using some scaling functions

isobianin, 2020-10-14:
Hi @amchagas !

I have been able to finish the task and I would like you to look at it at my [fork](https://github.com/isobianin/Flypi/tree/master/GUI_2.1). Now there are scrollareas for each tab and they all are nicely incorporated into the current design. 

In the **main.py** I changed one line of code:

if __name__ == "__main__":
... dialog = QtWidgets.QMainWindow() ...

I believe that this is important because this function enables setCentralWidget function which was commented out in flypi_GUI.py

**flypi_GUI.py** was changed substantially but everything remains operational. What I mean is that the graph library is present and corresponding line of code that connects pyqtgraph with the graph is also there. Also, I found it strange that two scrollbars that are in the "camera" tab (horiz and vertical offsets) did not work when clicked on arrows. Now they can be clicked with an increment of 1.

[image]
Fig. 1 - Updated UI

isobianin, 2020-10-16:
Hi @amchagas !

I have tinkered with UI a bit more and now it looks the way it is supposed to look. I have updated backgrounds of scrollareas so they match the previously chosen style (fig. 1)
[image]

isobianin, 2020-10-16:
An additional screenshot of how scrolls work with an example of the "protocol" tab
[image]

amchagas, 2020-10-16:
Hi @isobianin , this looks great,
I am very short on time until Tuesday, but will give it a try then! 
Thanks again for putting time and effort into this!!

amchagas, 2020-12-04:
Sorry, I completely forgot to update this one! The UI looks quite nice and the scrollbars work very well!

amchagas, 2020-12-04:
should probably only close this when we do the PR

isobianin, 2020-12-04:
Hi @amchagas !
Okay, I guess that will do

wexterhack, 2021-01-13:
As I understand this task is closed?

amchagas, 2021-01-18:
Hi @wexterhack yes, this has been dealt with! 
thanks for the interest!

closed 2021-01-18 by amchagas

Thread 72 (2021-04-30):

amchagas/Flypi #72: BOM obsolete parts

neurologic, 2021-04-30:
Hi,
The digikey cart almost fills completely using the current BOM but there are two obsolete parts.
Would you be able to advise on appropriate replacements that fit the specs of the unit and also match the footprint on the gerber?
[image]
https://www.digikey.com/en/products/detail/parallax-inc/452-00007/7791449?s=N4IgTCBcDaICwFYwFoAM7UHZkDkAiIAugL5A
and
https://www.digikey.com/en/products/detail/osram-sylvania-inc/LZ1-10UB00-00U4/5034037

Thank you!

neurologic, 2021-04-30:
I am also having trouble finding a replacement for a backordered part (45 weeks lead time) for component #U4 (IC BRIDGE DRIVER PAR 15MULTIWATT)

amchagas, 2021-05-06:
Hi!
thanks for raising up the obsolete part at DigiKey. I just pushed some changes with a new part that should work. 
For the other parts, dpending on where you are, you could get them  (or very similar ones) from ebay/amazon...
let me know if this solves this issue?

neurologic, 2021-05-07:
Hi Andres. I just saw that push! Thank you!

neurologic, 2021-05-07:
(I am in Connecticut, USA) I used a combination of DigiKey, Mouser, Newark, and Jameco to get all of the parts. A lot was on backorder at each place, but with a combination of all sources  I think I was able to get almost all of the specified parts. I suspect the pandemic is currently a major source effecting supply of component parts? The one item I still was not able to get were the pin housings. But in a pinch, I suppose I am thinking that it looks like I can jump the pins directly to the board from each component?

neurologic, 2021-05-07:
@amchagas, I have another related question. Do you have a recommendation for a "reflective collimator"? I don't see one in the parts list and when I google that term, I can't find something that looks like the silver collar that I see on page 21 of the FlyPi User and Assembly Manual. Should it be something that fits into the "strongLED_holder" printed part? I can't tell from the figure in that assembly pdf, how those pieces fit together and inside of each other. Any help greatly appreciated. Thank you! (If you had any opportunity to have a video chat about the FlyPi set up let me know. I am really excited to set it up for the course I am teaching next semester, but I feel pretty shaky on the details of actually implementing.) I am very very stoked on your design and its applicability.

amchagas, 2021-05-21:
Hi @neurologic ! 
Very sorry about the delay in replying... closing some projects at work plus a small child at home has done me in for the last 2 weeks... 
We can catch up via a video call, sure! Send me an email on a.maia-chagas@sussex.ac.uk (or send me an email address so I can send you a message to arrange things)!

neurologic, 2021-05-26:
Thank you, @amchagas. This sounds great. Sorry for the delay as well. It sounds like we are in some similar situation! I have what still feels like a very new 7month old.
I have all of the parts in now (I think) and am starting to assemble the PCB (rev. 0.6 20171203). And I think I figured my way through the orientation of the 3D parts (and have some notes on edits). I would be happy to try to work on a revised assembly guide while I work through assembling. Meeting to talk about an overview would help a lot since I am pretty novice still at a lot of the electronic circuit principles (but am pretty comfortable with Linux, python, etc so that helps). 
I will email you now.

closed 2021-05-27 by amchagas

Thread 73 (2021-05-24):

amchagas/Flypi #73: peltier module not cooling

rjs360, 2021-05-24:
Hi all,
My build is a v. 2.0, running GUI 2.2. 

Aside from a non-responsive servo module (if anyone has run into this issue please let me know), all seemed to be working fine (all the lighting options are working great) until I tried the peltier module. It heats up fine, e.g. to 35C, but when I try to cool to 15C, it will not cool beyond 25C. I have a heatsink attached to the peltier module, and a fan blowing at it (according to instructions).

Anyone run into this issue? Do I just need more powerful cooling?
Thanks for any insight.
-Ruud

amchagas, 2021-05-27:
Hi @rjs360 !
Cool that you set up a FlyPi, bummer that there are still some glitches. 
Could you share a bit more details on the Peltier, fan and heatsink? 

The reason I ask is that since you have the heatsink and fan, it should work (also considering that most of other things are working as well)...

Another question is how much time does it take to heat from room temp to 35C?

In principle you should not need more powerful cooling...

rjs360, 2021-05-27:
Hi @amchagas, thanks for the reply!  
Yep a couple of bumps in the road but that makes things fun (mostly ;)).

The peltier is a CP85438 (or TEC127050), through DigiKey (102-1682-ND; as listed in the BOM); the fan is a 36x36mm 5V fan, through DigiKey (P19864-ND; as listed in the BOM); the heatsink is the 36x36x12 heatsink (digikey 294-1101-ND) listed in the BOM.  

Heating to 35C is no problem, it takes ~30s to get to 35C from 21C ambient.
I wonder if my thermistor maybe bad?

Additionally, lighting all works fine, servo doesn't, but i worked around that.
-R

rjs360, 2021-05-27:
Make that temp. sensor (AD22100KTZ) instead of thermistor..

amchagas, 2021-05-27:
What PCB board revision do you have?

amchagas, 2021-05-27:
maybe there is another case of board mislabelling?

rjs360, 2021-05-27:
Looks like rev. 0.6
-Ruud

rjs360, 2021-05-28:
Just adding to this: I do get expected values for ambient temperatures using my current wiring. I tried reversing the +/- on the thermistor but that gives me values of about ~150-152 as "ambient" temperatures.  By the way, the latest PCB gerber file (the one that was changed 16 days ago) seems to indicate +S- (from left to right, seen from the top) for the thermistor connector. Did this get changed? My rev. 0.6 board has -S+, but again, reverse wiring does not give expected numbers.  Any thoughts would be welcome, would like to get this sorted out.

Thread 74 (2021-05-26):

amchagas/Flypi #74: PyQt5.sip

neurologic, 2021-05-26:
Hi,
I am working on trying to get the GUI running. I have solved some roadblocks that I have come across so far, but can't get past this one yet after a couple of hours of searching and troubleshooting. So I thought it was time to reach out. Did you do anything special to get PyQt5 installed on your Raspberry Pi with PyQt5.sip as a module? 

I was finally able to get PyQt5 using $ sudo apt-get install python3-pyqt5
But there was not PyQt5.sip module.
I tried making sip from source as PyQt5.sip and that worked... but then there was another PyQt module that was missing and I could not make the dependencies match.

Then I tried installing miniconda thinking that it should have all of these modules. It almost worked. I am still getting an error (now for PyCapsule_GetPointer called with the wrong name). In searching it sounded like downgrading PyQt5 to 5.10.1 would solve that. But I cannot seem to do so. 

Did you have troubles with this? Do you have an environment file that you could share (though I only know how to do that in conda)?

Any insight would be great.

neurologic, 2021-05-26:
Also, I don't know if this is correct or not, but I was going into the GUI_2.2 folder to run the flypi_GUI.py using python3. Given the folders and files available I was surmising that this was correct (as opposed to "sudo python3 ./run.py" instructed in the PDF... it looks like that was for GUI_1.0?)

neurologic, 2021-05-26:
I did try to go into GUI_1.0 and do "python run.py" and a GUI window did generate! Is this what I should still be using? Since there were so many #2 versions and I was working with the newest board version I assumed I should use the 2.x GUIs.

neurologic, 2021-05-27:
I am so happy. I got the GUI_2.2 to run (on my MacOS). I had to change the serial port in main.py. I don't know how to include that as an input variable to the script, but in the near future if I learn how to push some edits to this package I will work on that. 

Now I will try again on my Rpi! Troubleshooting on the Rpi had been frustrating because I have a really really old very slow one and it was hard to learn on. Now that I learned a lot today about the backend I think I might be able to work through some of the issues I was having on the Rpi yesterday. 

[image]

amchagas, 2021-05-27:
Hi, 

Great that you got the GUI to run on another system. And yeah, each operating system treats the serial port in a different way/different nomenclature (in Windows they are COMX - with X being a "random" number for that port, in Linux ttyUSB0 for the Arduino nano and ttyACM0 for the Arduino uno -  no idea for macs.. never used them :P )

About installing things on the Pi, If you have a Raspberry Pi 3 we do provide an image that you can use to create the SD card, which I think is updated and has all things installed, so you should be able to simply run the GUI without having to install anything.. it is here https://www.dropbox.com/s/12o271wj37rqkj6/flypi_image.zip?dl=0

neurologic, 2021-05-27:
Thank you so much, @amchagas . I did see in the documents that there was an image to use. I was avoiding the image in the short term since I had other things running on the RPi and only one SD card currently. 
I don't really know how (but I took some notes)... but I finally got the packages needed and talking nicely with each other. For me it ended up involving downgrading pyqtgraph to 5.11 because PyQt5 install on Pi that I could figure out did not support 5.12 (I think?). And then realizing that I needed to run the code as sudo. 

I was able to hook up and operate the LED ring and the peltier modules! The temperature tracked well and the ring colors all worked. 
There were some edits that seem to be needed that I took note of (for example, some of the +/-/signal notation on the PCB print was mixed up). 

There are some additional edits that I need to make to the code and some questions that I have about getting the optogenetic experiments to work (I am confused which LEDs are expected to be used for this and how). For now it seems I have gotten the hardware and software up and running for the most part. 

I emailed you recently to talk about having a video chat. I have started to try to figure out how to edit the code, but it would be more informative to talk to you about some of these things if you are open to it. We can talk about how I can help revise the assembly PDF, etc as well if you are interested. 

I am also working on a odor delivery system for an electro-antennae-gram experiment in my course. It currently runs off of RaspberryPi through adafruit Crickit. But I would like to translate it to be run by the nano so that I could add a module into your gui for the course (if you are interested in me sharing that with you when I am finished let me know). 

This is a lot of fun. Thank you for putting this all together and sharing!

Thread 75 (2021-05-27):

amchagas/Flypi #75: Arduino Serial Command

neurologic, 2021-05-27:
Hi,
It's me again. I know you are very busy so don't want to create too many 'issues'. I am solving things where I can (and learning a lot). I came across a new issue that I think I know how to get around but am not sure.  At some point, I can learn how to propose/contribute edits via git (I have never done that before and have not been good at following branching protocol, etc in my life; but want to).

Today I am trying to get the Arduino code going so that the Rpi GUI can communicate.  (Yesterday I got GUI_1.0 working on my Rpi but only with the camera module). Today I learned how to communicate with Arduino via Python and serial! (I was learning using pyfirmata). So I think I am understanding the premise behind the FlyPi communication setup between the Rpi and the PCB/Nano. 

So from what I understand currently, you have written arduino code that sets it up to receive commands via python directly (analagous to the pyfirmata 'standard' script that I was loading earlier today onto my nano to control via python). I am working with the most recent script found in the v2 folder called 'serial_test'.

I solved some Library import issues with the adafruit packages by adding via zip downloaded from git directly and found Stephen Cogswell's 'SerialCommand.h' at ```https://github.com/scogswell/ArduinoSerialCommand/blob/master/SerialCommand.h, which I used to 'add library via zip'```.

The #include works for this, but it seems like one of the modules called in your arduino script is not (no longer?) a part of their library. 

ArduinoIDE check fails on:
 ```sCmd.setDefaultHandler(unrecognized);      // Handler for command that isn't matched  (says "What?")```

Looking at Stephen's code, it seems like the command might have changed to 'addDefaultHandler'?
```void addDefaultHandler(void (*function)());    // A handler to call when no valid command received. ```

I edited the Arduino code for addDefaultHandler for now. 
When I did this, the IDE compilation completed.
BUT I do get the following orange text:
```
<my filepath>/Flypi/Arduino/v2.0/serial_test/serial_test.ino: In function 'void setup()':
<my filepath>/Flypi/Arduino/v2.0/serial_test/serial_test.ino:120:38: warning: invalid conversion from 'void (*)(const char*)' to 'void (*)()' [-fpermissive]
   sCmd.addDefaultHandler(unrecognized);      // Handler for command that isn't matched  (says "What?")
                                      ^
In file included from <my filepath>/Flypi/Arduino/v2.0/serial_test/serial_test.ino:31:0:
<my filepath>/Arduino/libraries/ArduinoSerialCommand_master/SerialCommand.h:85:8: note:   initializing argument 1 of 'void SerialCommand::addDefaultHandler(void (*)())'
   void addDefaultHandler(void (*function)());    // A handler to call when no valid command received.
```

Let me know if you think this is an error that I am missing a step somewhere or have the wrong library. 

Also, for the adafruit libraries, my includes ended up looking like this to make it work:

```

#include <Adafruit_NeoPixel.h> // LED Ring

#include <Wire.h> // LED Matrix
//#include <Adafruit_LEDBackpack.h> // LED Matrix
//#include <Adafruit_GFX.h> // LED Matrix

#include <Adafruit_LEDBackpack.h>

#include <Adafruit_GrayOLED.h>
#include <gfxfont.h>
#include <Adafruit_GFX.h>
#include <Adafruit_SPITFT.h>
#include <Adafruit_SPITFT_Macros.h>
```

neurologic, 2021-05-27:
Interesting. For other reasons I just ended up at what is pointed from Stephen's site as 'an alternative':
```https://github.com/kroimon/Arduino-SerialCommand/blob/master/SerialCommand.h```

This one has 'setDefaultHandler'! So this must be the one that you are pointing to/including. 

I just tried that... and it worked without error or orange text! 
So I think I ended up solving this. Hopefully this info is helpful to someone else who might come across the same hiccup.

amchagas, 2021-05-27:
Glad you worked this one out! 
One comment on this one: 

V1.0 of the GUI requires V1.0 of the arduino code, where we are not using the serial library you mention (as far as I remember)...
 
Just in case the communication between the two boards do not work...

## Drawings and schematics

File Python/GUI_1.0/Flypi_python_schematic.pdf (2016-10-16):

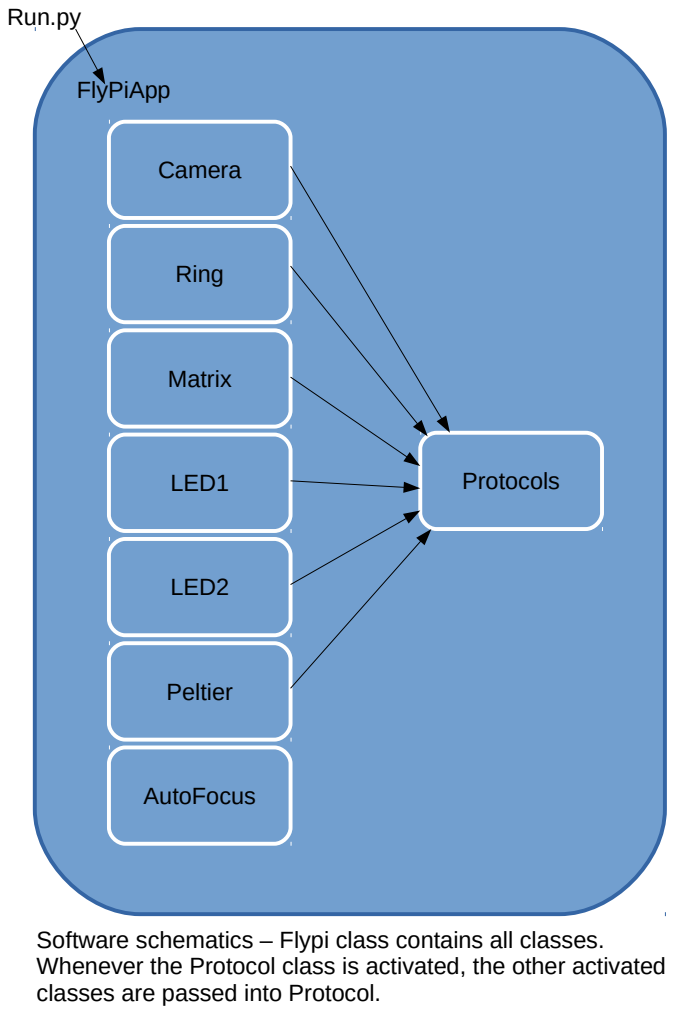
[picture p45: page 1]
FlyPiApp; Ring; Matrix; LED1; LED2; Peltier; AutoFocus; Camera; Protocols; Run.py

Software schematics – Flypi class contains all classes.
Whenever the Protocol class is activated, the other activated
classes are passed into Protocol.

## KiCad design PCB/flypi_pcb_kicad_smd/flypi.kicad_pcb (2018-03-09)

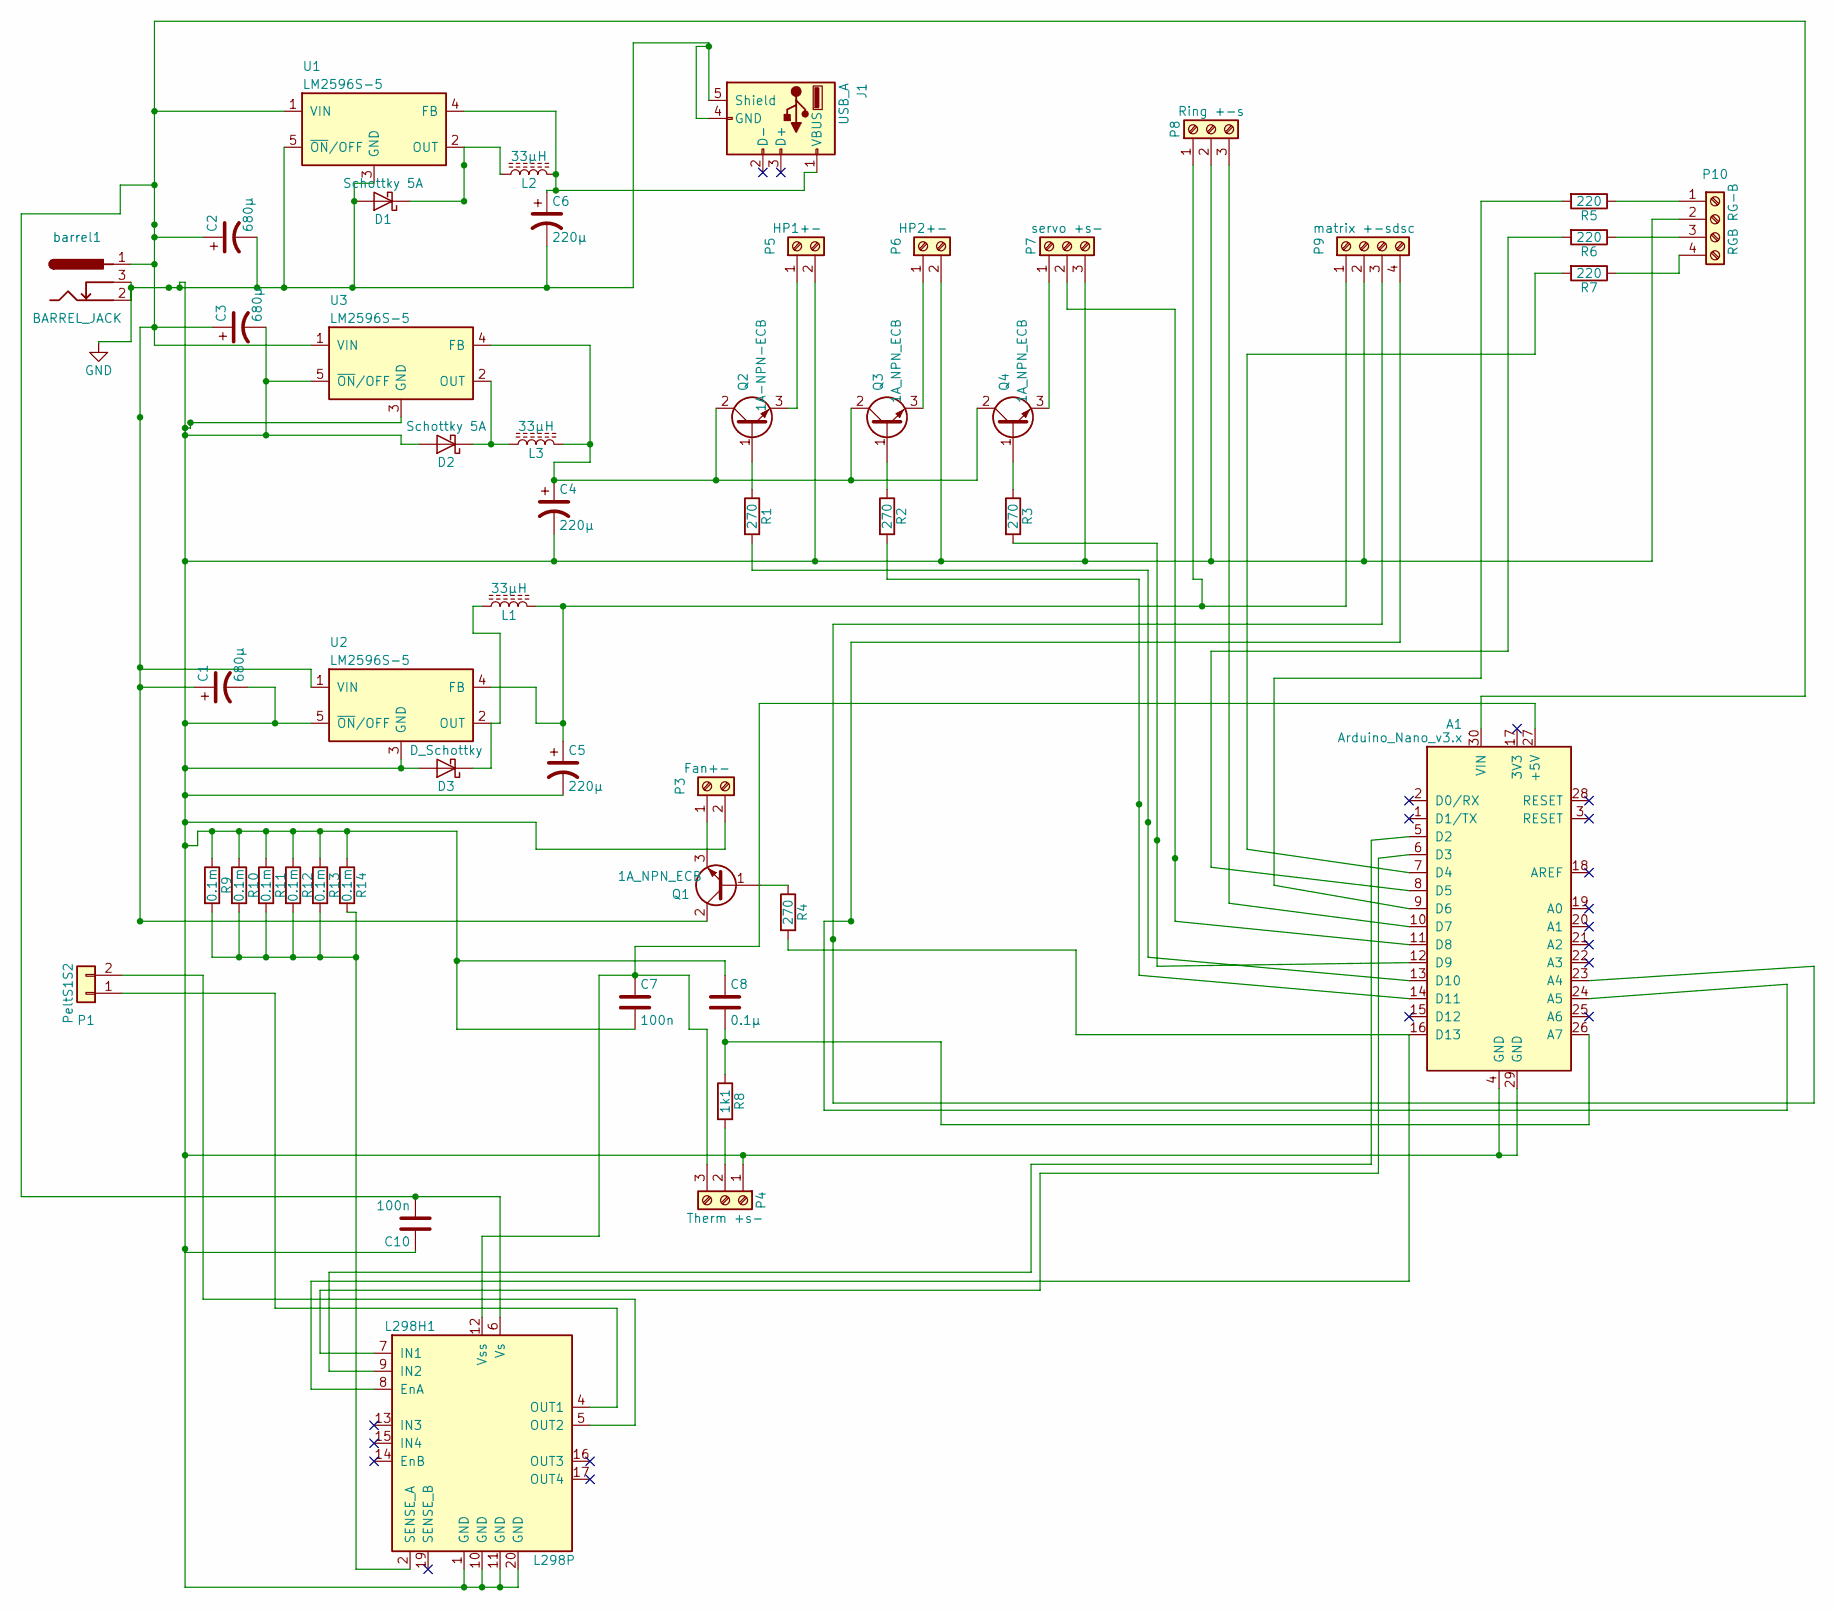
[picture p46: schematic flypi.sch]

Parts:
A1: Arduino_Nano_v3.x; Arduino_Nano
C1, C2, C3: 680µ; CP_Elec_10x10
C4, C5, C6: 220µ; CP_Elec_6.3x5.3
C7, C10: 100n; C_0805_HandSoldering
C8: 0.1µ; C_0805_HandSoldering
D1, D2: Schottky 5A; D_SMB-SMC_Universal_Handsoldering
D3: D_Schottky; D_SMB-SMC_Universal_Handsoldering
J1: USB_A; USB_A_Vertical
L1, L2, L3: 33µH; L_6.3x6.3_H3
L298H1: L298P; HSOP-20-1EP_11.0x15.9mm_Pitch1.27mm_SlugUp
P1: PeltS1S2; JST_EH_S02B-EH_02x2.50mm_Angled
P3: Fan+-; JST_EH_S02B-EH_02x2.50mm_Angled
P4: Therm +s-; JST_EH_S03B-EH_03x2.50mm_Angled
P5: HP1+-; JST_EH_S02B-EH_02x2.50mm_Angled
P6: HP2+-; JST_EH_S02B-EH_02x2.50mm_Angled
P7: servo +s-; JST_EH_S03B-EH_03x2.50mm_Angled
P8: Ring +-s; JST_EH_S03B-EH_03x2.50mm_Angled
P9: matrix +-sdsc; JST_EH_S04B-EH_04x2.50mm_Angled
P10: RGB RG-B; JST_EH_S04B-EH_04x2.50mm_Angled
Q1, Q3, Q4: 1A_NPN_ECB; SOT-89-3_Handsoldering
Q2: 1A-NPN-ECB; SOT-89-3_Handsoldering
R1, R2, R3, R4: 270; R_2816_HandSoldering
R5, R6, R7: 220; R_2816_HandSoldering
R8: 1k1; R_2816_HandSoldering
R9, R10, R11, R12, R13, R14: 0.1m; R_1812_HandSoldering
U1, U2, U3: LM2596S-5; TO-263-5_TabPin3
barrel1: BARREL_JACK; Barrel_Jack_CUI_PJ-102AH
gnd1: GND

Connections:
GND: A1.4 (GND), A1.29 (GND), C1.2, C2.2, C3.2, C4.2, C5.2, C6.2, C7.2, C8.1, C10.1, D1.2 (A), D2.2 (A), D3.2 (A), J1.4 (GND), J1.5 (Shield), L298H1.1 (GND), L298H1.10 (GND), L298H1.11 (GND), L298H1.20 (GND), P3.2, P4.1, P5.2, P6.2, P7.3, P8.2, P9.2, P10.2, R9.1, R10.1, R11.1, R12.1, R13.1, R14.1, U1.3 (GND), U1.5 (~ON~/OFF), U2.3 (GND), U2.5 (~ON~/OFF), U3.3 (GND), U3.5 (~ON~/OFF), barrel1.2, barrel1.3, gnd1.1
unnamed: A1.5 (D2), L298H1.9 (IN2)
unnamed: A1.6 (D3), L298H1.7 (IN1)
unnamed: A1.7 (D4), R7.2
unnamed: A1.8 (D5), R6.2
unnamed: A1.9 (D6), R5.2
unnamed: A1.10 (D7), P8.3
unnamed: A1.11 (D8), P7.2
unnamed: A1.12 (D9), R3.2
unnamed: A1.13 (D10), R1.2
unnamed: A1.14 (D11), R2.2
unnamed: A1.16 (D13), L298H1.8 (EnA), R4.2
unnamed: A1.23 (A4), P9.3
unnamed: A1.24 (A5), P9.4
unnamed: A1.26 (A7), C8.2, R8.1
unnamed: A1.27 (+5V), C7.1, L298H1.12 (Vss), P4.3
unnamed: A1.30 (VIN), C1.1, C2.1, C3.1, C10.2, L298H1.6 (Vs), Q1.2 (C), U1.1 (VIN), U2.1 (VIN), U3.1 (VIN), barrel1.1
unnamed: C4.1, L3.2, Q2.2 (C), Q3.2 (C), Q4.2 (C), U3.4 (FB)
unnamed: C5.1, L1.2, P8.1, P9.1, U2.4 (FB)
unnamed: C6.1, J1.1 (VBUS), L2.2, U1.4 (FB)
unnamed: D1.1 (K), L2.1, U1.2 (OUT)
unnamed: D2.1 (K), L3.1, U3.2 (OUT)
unnamed: D3.1 (K), L1.1, U2.2 (OUT)
unnamed: L298H1.2 (SENSE_A), R9.2, R10.2, R11.2, R12.2, R13.2, R14.2
unnamed: L298H1.4 (OUT1), P1.1
unnamed: L298H1.5 (OUT2), P1.2
unnamed: P3.1, Q1.3 (E)
unnamed: P4.2, R8.2
unnamed: P5.1, Q2.3 (E)
unnamed: P6.1, Q3.3 (E)
unnamed: P7.1, Q4.3 (E)
unnamed: P10.1, R5.1
unnamed: P10.3, R6.1
unnamed: P10.4, R7.1
unnamed: Q1.1 (B), R4.1
unnamed: Q2.1 (B), R1.1
unnamed: Q3.1 (B), R2.1
unnamed: Q4.1 (B), R3.1

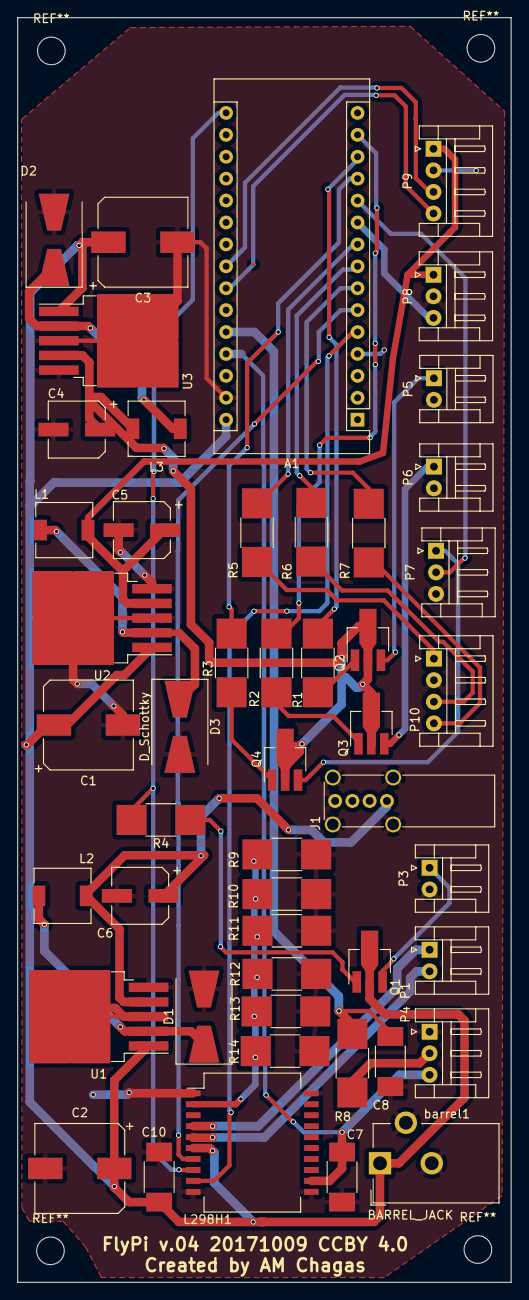
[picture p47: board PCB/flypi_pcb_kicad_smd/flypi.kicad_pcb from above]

Board: 2 copper layers, 57.2 x 146.6 mm, 49 parts (0 on the bottom side), 38 nets.

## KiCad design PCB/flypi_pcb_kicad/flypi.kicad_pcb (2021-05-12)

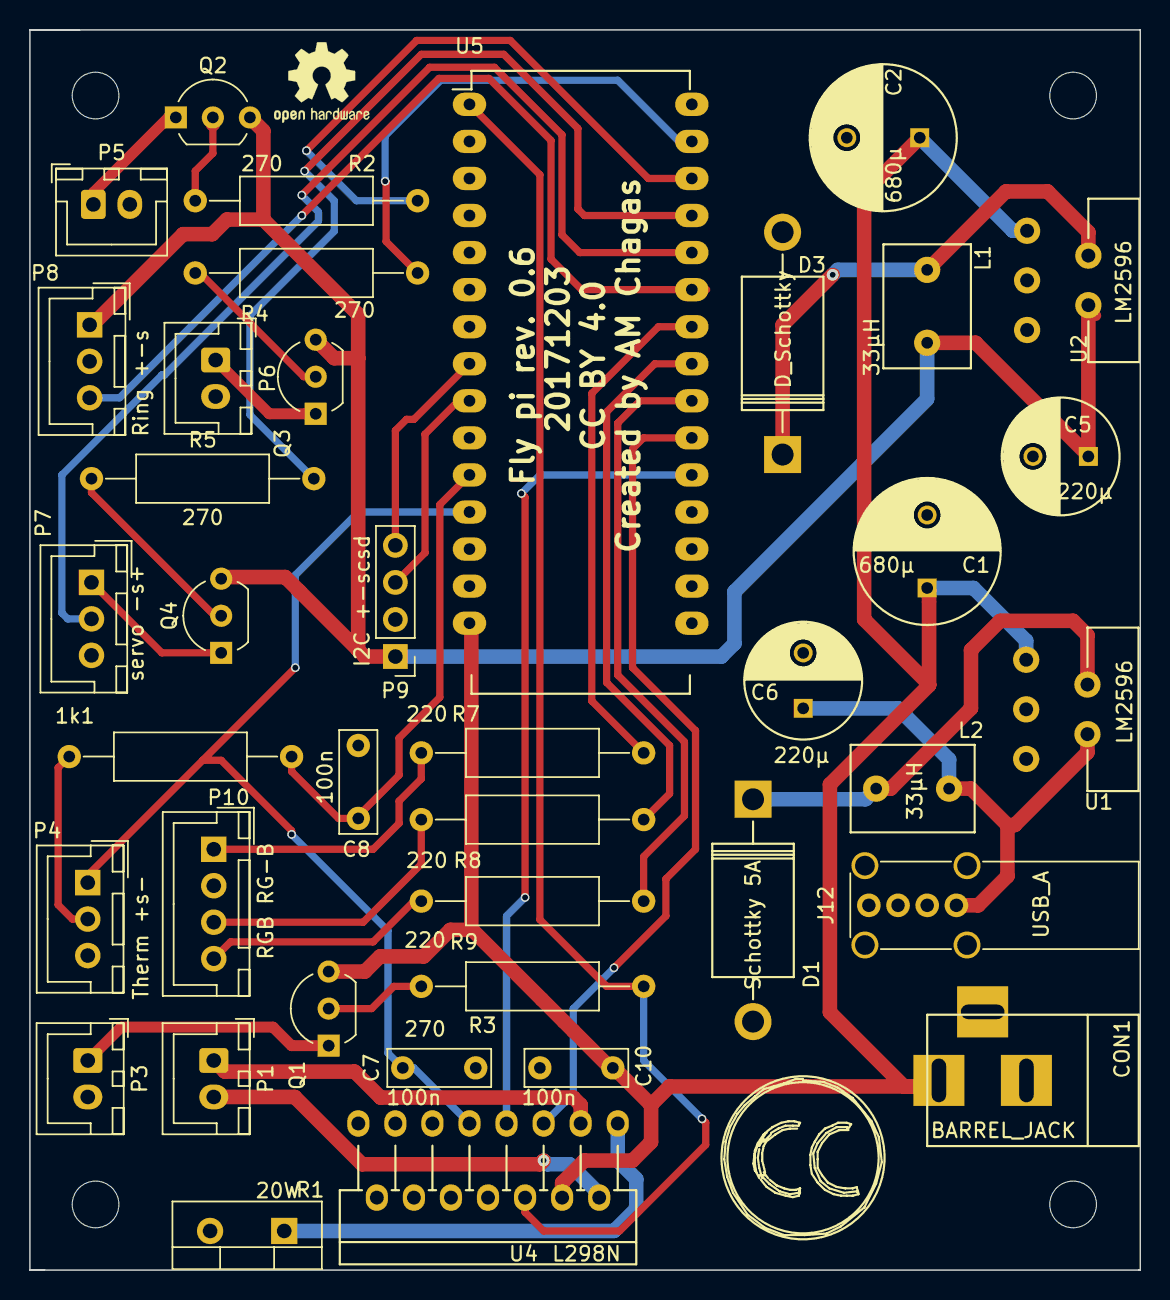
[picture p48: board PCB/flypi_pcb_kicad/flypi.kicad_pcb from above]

Board: 2 copper layers, 76.1 x 85.0 mm, 40 parts (0 on the bottom side), 36 nets.

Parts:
1k1: R; R_Axial_DIN0309_L9.0mm_D3.2mm_P15.24mm_Horizontal
 : MountingHole_3.2mm_M3_DIN965
C1, C2: 680µ; C_Radial_D10_L21_P5
C5, C6: 220µ; C_Radial_D8_L13_P3.8
C7, C8, C10: 100n; C_Rect_L7.0mm_W2.5mm_P5.00mm
CON1: BARREL_JACK
D1: Schottky 5A; Diode_DO-201AD_Horizontal_RM15
D3: D_Schottky; Diode_DO-201AD_Horizontal_RM15
J12: USB_A; USB_A_Vertical
L1, L2: 33µH; Neosid_Inductor_MA-Bs75
P1: PeltS1S2; JST_XH_B2B-XH-A_1x02_P2.50mm_Vertical
P3: Fan+-; JST_XH_B2B-XH-A_1x02_P2.50mm_Vertical
P4: Therm +s-; JST_XH_B03B-XH-A_03x2.50mm_Straight
P5: HP1+-; JST_XH_B2B-XH-A_1x02_P2.50mm_Vertical
P6: HP2+-; JST_XH_B2B-XH-A_1x02_P2.50mm_Vertical
P7: servo -s+; JST_XH_B03B-XH-A_03x2.50mm_Straight
P8: Ring +-s; JST_XH_B03B-XH-A_03x2.50mm_Straight
P9: I2C +-scsd; Socket_Strip_Straight_1x04_Pitch2.54mm
P10: RGB RG-B; JST_XH_B04B-XH-A_04x2.50mm_Straight
Q1, Q3, Q4: 1A_NPN_EBC; TO-92_Inline_Wide
Q2: 1A-NPN-EBC; TO-92_Inline_Wide
R1: 20W; TO-220-2_Vertical
R2, R3, R4, R5: 270; R_Axial_DIN0309_L9.0mm_D3.2mm_P15.24mm_Horizontal
R7, R8, R9: 220; R_Axial_DIN0309_L9.0mm_D3.2mm_P15.24mm_Horizontal
U1, U2: LM2596
U4: L298N; Multiwatt_15_Vertical
U5: arduino_mini; DIP-30_W15.24mm_LongPads

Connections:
GND: C1.2, C2.2, C5.2, C6.2, C7.2, C8.1, C10.1, CON1.2, CON1.3, D1.2, D3.2, J12.4, J12.5, P3.2, P4.3, P5.2, P6.2, P7.3, P8.2, P9.2, P10.2, R1.2, U1.3, U1.5, U2.3, U2.5, U4.8, U5.14, U5.19
unnamed: 1k1.1, C8.2, U5.11
unnamed: 1k1.2, P4.2
unnamed: C1.1, C2.1, C10.2, CON1.1, Q1.3, U1.1, U2.1, U4.4, U5.15
unnamed: C5.1, L1.2, P8.1, P9.1, Q2.3, Q3.3, Q4.3, U2.4
unnamed: C6.1, J12.1, L2.2, U1.4
unnamed: C7.1, P4.1, U4.9, U5.12
unnamed: D1.1, L2.1, U1.2
unnamed: D3.1, L1.1, U2.2
unnamed: P1.1, U4.3
unnamed: P1.2, U4.2
unnamed: P3.1, Q1.1
unnamed: P5.1, Q2.1
unnamed: P6.1, Q3.1
unnamed: P7.1, Q4.1
unnamed: P7.2, U5.26
unnamed: P8.3, U5.25
unnamed: P9.3, U5.9
unnamed: P9.4, U5.8
unnamed: P10.1, R7.1
unnamed: P10.3, R8.1
unnamed: P10.4, R9.1
unnamed: Q1.2, R3.1
unnamed: Q2.2, R2.1
unnamed: Q3.2, R4.1
unnamed: Q4.2, R5.1
unnamed: R1.1, U4.1
unnamed: R2.2, U5.28
unnamed: R3.2, U4.6, U5.1
unnamed: R4.2, U5.29
unnamed: R5.2, U5.27
unnamed: R7.2, U5.24
unnamed: R8.2, U5.23
unnamed: R9.2, U5.22
unnamed: U4.5, U5.21
unnamed: U4.7, U5.20

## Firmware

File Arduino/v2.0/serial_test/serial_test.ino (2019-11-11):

// FlyPi Arduino control code    //
// Dev. by AM Chagas             //
// 20190702 CC BY SA 4.0         //

// dependencies:
// Adafruit libraries for
//  - LED Matrix
//  - LED Ring
// SerialCommand Library by Steven Cogswell




// Import libraries

#include <Adafruit_NeoPixel.h> // LED Ring

#include <Wire.h> // LED Matrix
#include <Adafruit_LEDBackpack.h> // LED Matrix
#include <Adafruit_GFX.h> // LED Matrix

#include <Servo.h> //servo motor controlling the autofocus
#include <SerialCommand.h>




#include "peltier.h"
#include "ring.h"
#include "matrix.h"
#include "servo.h"


// define ports
#define LED1Pin 10
#define LED2Pin 11
#define servoPin 8
#define servoOnPin 9






//Timing Variables////////////////////////
long int millistowait;




////////////////////////////////////////

SerialCommand sCmd;     // The demo SerialCommand object

void setup() {
  
  pinMode(LED1Pin, OUTPUT);
  pinMode(LED2Pin, OUTPUT);

  pinMode(RedGBPin, OUTPUT);
  pinMode(RGreenBPin, OUTPUT);
  pinMode(RGBluePin, OUTPUT);

  pinMode(servoOnPin, OUTPUT);

  pinMode(peltierEnablePin, OUTPUT);
  pinMode(peltierHeatPin1, OUTPUT);
  pinMode(peltierCoolPin1, OUTPUT);

  focusServo.attach(servoPin);
  // start ring
  pixels.begin();

  Serial.begin(115200);

  // Setup callbacks for SerialCommand commands //////


  sCmd.addCommand("S1",    SERVO_on);
  sCmd.addCommand("S0",    SERVO_off);

  sCmd.addCommand("M1",    MATRIX_on);
  //sCmd.addCommand("M0",    MATRIX_off);
  //sCmd.addCommand("M11",    MATRIX_pat1);
  //sCmd.addCommand("M12",    MATRIX_pat2);
  //sCmd.addCommand("M13",    MATRIX_pat3);
  //sCmd.addCommand("M14",    MATRIX_bright);




  sCmd.addCommand("L11",    LED1_on);          // Turns LED1 on and sets intensity
  sCmd.addCommand("L10",    LED1_off);         // Turns LED1 off

  sCmd.addCommand("L21",    LED2_on);          // Turns LED2 on
  sCmd.addCommand("L20",    LED2_off);         // Turns LED2 off

  sCmd.addCommand("R1",     RING_on);          // Turns RING on
  sCmd.addCommand("R0",     RING_off);         // Turns RING off
  sCmd.addCommand("RR",     RED);              // change RED intensity
  sCmd.addCommand("RG",     GREEN);            // change GREEN intensity
  sCmd.addCommand("RB",     BLUE);             // change BLUE intensity

  sCmd.addCommand("P1",     PELT_on);          // Turns PELTIER on
  sCmd.addCommand("P0",     PELT_off);         // Turns PELTIER off
  sCmd.addCommand("ST",     PELT_stemp);       // set PELTIER temperature
  sCmd.addCommand("GT",     TEMP_read);        // get PELTIER temperature
  sCmd.addCommand("TW",     TIME_wait);        // sets time to wait


  sCmd.addCommand("HELLO", sayHello);        // Echos the string argument back
  sCmd.addCommand("P",     processCommand);  // Converts two arguments to integers and echos them back
  sCmd.setDefaultHandler(unrecognized);      // Handler for command that isn't matched  (says "What?")

  // turn everything off
  digitalWrite(servoOnPin, LOW);
  //matrix.clear();
  //matrix.writeDisplay();
  updateRing(0, 0, 0, 0);
  pixels.show();
  analogWrite(LED1Pin, 0);
  analogWrite(LED2Pin, 0);
  Serial.println("Ready");
  digitalWrite(peltierEnablePin,LOW);
  digitalWrite(peltierHeatPin1, LOW);
  digitalWrite(peltierCoolPin1, LOW);

  newTemp = checkTemp(tempSensorPin);


  pixels.setPixelColor(0, pixels.Color(0,0,0));
  pixels.show();
}

void loop() {

  sCmd.readSerial();     // We don't do much, just process serial commands

}// void loop


///////// servo callbacks ////////////////////////////
void SERVO_on(){
  servoOn = 1;
  int aNumber;
  char *arg;
  arg = sCmd.next();

  if (arg != NULL) {

    if (atoi(arg) == 90){
      digitalWrite(servoOnPin, LOW);
      }//end if arg==90

    else {
    digitalWrite(servoOnPin, HIGH);
    focusServo.write(atoi(arg)); //because this is a cont. servo,
    //this will set the velocity, not the pos.
    delay(15);
    }//end else
    }// if arg!=NULL
  waited();

  }//servo_on

void SERVO_off(){
  servoOn = 0;
  digitalWrite(servoOnPin, LOW);
  waited();
  }


/////////matrix callbacks ////////////////////////////
void MATRIX_on(){
  matrixOn = 1;
  matrix.writeDisplay();
  waited();
  }

void MATRIX_off(){
  matrixOn = 0;
  matrix.clear();
  matrix.writeDisplay();
  waited();
  }
/*
void MATRIX_bright(){
  updateMatrix()
  matrix.setBrightness(matrix_brightness);

  if (matrixOn==1){
    matrix.writeDisplay();
  }
  waited();
  }
void MATRIX_pat1(){

   matrix.clear();
   matrix.drawBitmap(0, 0, matrix_pattern1, 8, 8, LED_ON);
   if (matrixOn == 1){
    matrix.writeDisplay(); // write changes to the display
   }
   waited();
  }
void MATRIX_pat2(){

   matrix.clear();
   matrix.drawBitmap(0, 0, matrix_pattern2, 8, 8, LED_ON);
   if (matrixOn == 1){
    matrix.writeDisplay(); // write changes to the display
   }//if
  waited();
  }
void MATRIX_pat3(){
  for (int i = 0; i < 4; i = i+1) {
     matrix.clear();
     if (i==0) {
        matrix.drawLine(0,0, 0,7, LED_ON);  matrix.drawLine(1,0, 1,7, LED_ON);
        matrix.drawLine(4,0, 4,7, LED_ON);  matrix.drawLine(5,0, 5,7, LED_ON); }
     if (i==1) {
        matrix.drawLine(1,0, 1,7, LED_ON);  matrix.drawLine(2,0, 2,7, LED_ON);
        matrix.drawLine(5,0, 5,7, LED_ON);  matrix.drawLine(6,0, 6,7, LED_ON); }
     if (i==2) {
        matrix.drawLine(2,0, 2,7, LED_ON);  matrix.drawLine(3,0, 3,7, LED_ON);
        matrix.drawLine(6,0, 6,7, LED_ON);  matrix.drawLine(7,0, 7,7, LED_ON); }
      if (i==3) {
        matrix.drawLine(3,0, 3,7, LED_ON);  matrix.drawLine(4,0, 4,7, LED_ON);
        matrix.drawLine(7,0, 7,7, LED_ON);  matrix.drawLine(0,0, 0,7, LED_ON); }
     if (matrixOn==1){
      matrix.writeDisplay(); // write changes to the display
     }//if matrix on
     delay(100); }
  waited();
  }
*/

/////////ring callbacks //////////////////////////////



void RING_on() {
  //Serial.println("ring on");
  ringOn = 1;
  updateRing(ringRedHue, ringGreenHue, ringBlueHue,ringOn);
  waited();
}

void RING_off() {
  //Serial.println("ring off");

  updateRing(0, 0, 0, ringOn);
  ringOn=0;
  waited();

  pixels.show();


  }


void RED(){
  int aNumber;
  char *arg;
  arg = sCmd.next();
  if (arg != NULL) {
     ringRedHue = atoi(arg);
     updateRing(ringRedHue, ringGreenHue, ringBlueHue,ringOn);
     waited();
  }//if

}//red

void GREEN(){
  int aNumber;
  char *arg;
  arg = sCmd.next();
  if (arg != NULL) {
     ringGreenHue = atoi(arg);
     updateRing(ringRedHue, ringGreenHue, ringBlueHue,ringOn);
     waited();
  }//if

}//red

void BLUE(){
  int aNumber;
  char *arg;
  arg = sCmd.next();
  if (arg != NULL) {
     //Serial.println("here");
     ringBlueHue = atoi(arg);
     updateRing(ringRedHue, ringGreenHue, ringBlueHue,ringOn);
     waited();
  }//if

}//red


////// LED functions ////////////////////////////////

void LED1_on() {
  int aNumber;
  char *arg;
  arg = sCmd.next();
  if (arg != NULL) {
     aNumber = atoi(arg);
     
     analogWrite(LED1Pin, aNumber);
     waited();
  }//if

}//led1_on

void LED1_off() {
  //Serial.println("LED1 off");
  analogWrite(LED1Pin, 0);
  waited();
}

void LED2_on() {
  int aNumber;
  char *arg;
  arg = sCmd.next();
  if (arg != NULL) {
     aNumber = atoi(arg);
     analogWrite(LED2Pin, aNumber);
     waited();
  }//if
}

void LED2_off() {
  //Serial.println("LED2 off");
  analogWrite(LED2Pin, 0);

  waited();
}


////////////////////////

//Peltier callbacks/////////////////


void PELT_on(){
  peltOn=1;
  digitalWrite(peltierEnablePin,HIGH);
  waited();
  //Serial.println("pelton");
}//pelt on


void PELT_off(){
  peltOn=0;
  digitalWrite(peltierEnablePin,LOW);
  digitalWrite(peltierHeatPin1, LOW);
  digitalWrite(peltierCoolPin1, LOW);
  analogWrite(RedGBPin, 0);
  analogWrite(RGreenBPin, 0);
  analogWrite(RGBluePin, 0);
  //Serial.println("waited()peltoff");
  waited();
}//pelt off

//peltier func (requiring scmd)
void PELT_stemp(){
   int aNumber;
   char *arg;
   arg = sCmd.next();
   if (arg != NULL) {
      newTemp = atoi(arg);
   }
   HoldTemp(newTemp, tempSensorPin,
                peltierCoolPin1,  peltierHeatPin1);

   waited();
  HoldTemp(newTemp, tempSensorPin,
               peltierCoolPin1, peltierHeatPin1);
}

void TEMP_read(){
  currTemp = checkTemp(tempSensorPin);
  //Serial.print("temp: ");
  Serial.println(currTemp);

  waited();
}//temp read


///////////////////////////////////////
// timing functions /////////////////

void TIME_wait(){

  long int aNumber;
  //int time1;
  //int time2;
  char *arg;
  long int time1=0;
  long int time2=0;

  time1 = millis();
  time2 = time1;

  arg = sCmd.next();
  if (arg != NULL) {
    aNumber = atol(arg);
    
    //Serial.println(aNumber);
    //wait amount of time
    while ((time1 - time2) < aNumber) {
    time1 = millis();
     } //done waiting


  }//if
  waited();
  }//time_wait


/////////////////////////////////////////



void sayHello() {

  char *arg;
  arg = sCmd.next();    // Get the next argument from the SerialCommand object buffer
  if (arg != NULL) {    // As long as it existed, take it
    Serial.print("Hello ");
    Serial.println(arg);
  }
  else {
    Serial.println("Hello, whoever you are");
  }
}


void processCommand() {
  int aNumber;
  char *arg;

  Serial.println("We're in processCommand");
  arg = sCmd.next();
  if (arg != NULL) {
    aNumber = atoi(arg);    // Converts a char string to an integer
    Serial.print("First argument was: ");
    Serial.println(aNumber);
  }
  else {
    Serial.println("No arguments");
  }

  arg = sCmd.next();
  if (arg != NULL) {
    aNumber = atol(arg);
    Serial.print("Second argument was: ");
    Serial.println(aNumber);
  }
  else {
    Serial.println("No second argument");
  }
}

// This gets set as the default handler, and gets called when no other command matches.
void unrecognized(const char *command) {
  Serial.println("What?");
}

void waited(){
  Serial.println("d");
  }

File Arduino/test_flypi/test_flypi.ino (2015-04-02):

/*this is a small test suite for the flypi.
  it is mainly used to make sure all parts connected to the 
  arduino are working properly. It acomplishes that by 
  turning each component on and off individually
  
  Written by A. Chagas and T. Baden*/
  
//import libraries for the LED ring
#include <Adafruit_NeoPixel.h> // LED Ring

//set pins
int tempPin=A7;
int tempRead=0;
int RedGBPin = 6;
int RGreenBPin = 4;
int RGBluePin = 5;
int RingPin = 7;
int peltierHeat1 =3;
int peltierHeat2 =13;
int peltierCool1 =2;
int peltierCool2 =12;

//set the number of LEDs in the ring
int Ring_nPixels = 12;
//create function to control LED ring
Adafruit_NeoPixel pixels = Adafruit_NeoPixel(Ring_nPixels, RingPin, NEO_GRB + NEO_KHZ800);

//things that are ran once
void setup (){
  //set the mode for the pins
  pinMode(RedGBPin,OUTPUT);
  pinMode(RGreenBPin,OUTPUT);
  pinMode(RGBluePin,OUTPUT);
  pinMode(peltierHeat1,OUTPUT);
  pinMode(peltierHeat2,OUTPUT);
  pinMode(peltierCool1,OUTPUT);
  pinMode(peltierCool2,OUTPUT);
  

  //initialize NeoPixel library (LED Ring).
  pixels.begin(); 
  //begin the serial port
  Serial.begin(9600);}

//start infinite loop
void loop (){
  
  //make sure everything is off
  digitalWrite(RedGBPin,LOW);
  digitalWrite(RGreenBPin,LOW);
  digitalWrite(RGBluePin,LOW);
  digitalWrite (peltierHeat1,LOW);
  digitalWrite (peltierHeat2,LOW);
  digitalWrite (peltierCool1,LOW);
  digitalWrite (peltierCool2,LOW);
  
  //test thermistor
  Serial.println("test temp sensor");
  for (int i=0; i<5;i+=1){
    //read the analog pin
    tempRead=analogRead(tempPin);
    //print it out for user
    Serial.println(tempRead);
    //1.5 sec interval
    delay(1500);}

  //test RGB
  Serial.println("test rgb led");
  digitalWrite(RedGBPin,HIGH);
  delay(500);
  digitalWrite(RedGBPin,LOW);
  delay(500);
  digitalWrite(RGreenBPin,HIGH);
  delay(500);
  digitalWrite(RGreenBPin,LOW);
  delay(500);
  digitalWrite(RGBluePin,HIGH);
  delay(500);
  digitalWrite(RGBluePin,LOW);
  delay(500);

  //test led ring
  Serial.println("test led ring");
    //change all LEDs in ring
    for (int i = 0; i < Ring_nPixels; i = i+1) { 
      // dim white
      pixels.setPixelColor(i, pixels.Color(5,5,5)); 
    }      
  // sends updated pixel color to hardware.  
  pixels.show(); 
  delay(500);
  for (int i = 0; i < Ring_nPixels; i = i+1) { 
    // dim white
    pixels.setPixelColor(i, pixels.Color(0,0,0)); 
   }      
  // sends updated pixel color to hardware.
  pixels.show(); 
  delay(500);

  //test peltier
  Serial.println("test peltier");

  //make it heat up and cool down three times
  for (int i=0;i<3;i+=1){
    //turn on the heat (assuming peltier has the correct side up)
    digitalWrite (peltierHeat1,HIGH);
    digitalWrite (peltierHeat2,HIGH);
    delay(2000);

    Serial.print("temperature: ");
    //print out temperature as read out by analog pin
    //make sure temperature sensor is working, before
    //blindly trusting these values
    Serial.println(analogRead(tempPin));
    //turn off the heat
    digitalWrite (peltierHeat1,LOW);
    digitalWrite (peltierHeat2,LOW);
    delay(1000);
    //turn on the cooling
    digitalWrite (peltierCool1,HIGH);
    digitalWrite (peltierCool2,HIGH);
    delay(2000);
    Serial.print("temperature: ");
    //print out temperature as read out by analog pin
    //make sure temperature sensor is working, before
    //blindly trusting these values
    Serial.println(analogRead(tempPin));
    //turn off the cooling
    digitalWrite (peltierCool1,LOW);
    digitalWrite (peltierCool2,LOW);
    }

}//end void loop

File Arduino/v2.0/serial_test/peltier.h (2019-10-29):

#define RedGBPin 6
#define RGreenBPin 4
#define RGBluePin 5
#define peltierEnablePin 13
#define peltierHeatPin1 3
#define peltierCoolPin1 2
#define tempSensorPin A7


//PELTIER variables ////////////////////////

float currTemp;
float newTemp;
float TempTol = 0.5; // tolerance
float highLimit = 40.0; //in Celsius
float lowLimit = 13.0; //in Celsius
int peltOn=0;


// function to get the temperature in °C by reading the AD22100 output
//to the analog in
float checkTemp(int pinToRead) {
  float temps = 0;
  float volts;
  float baseLine;
  for (int i = 0; i < 6; i++) {
    baseLine = analogRead(pinToRead);
    //temps = ((baseLine*(5.0 / 1023.0)) - 1.375) / 0.0225;
    //convert the value into volts
    volts = baseLine * (4750.0 / 1024);
    //convert the volt value into temperature (celsius)
    // the AD22100 has 200°C span (-50 to 150) for 4.5 V
    //therefore we need to subtract -1.375 to compensate
    //for this -50° offset
    temps = temps + ((volts - 1375) / 22.5);
    //delay(15);
  }//end for loop

  temps = temps / 5.0;
  //return the result of the function
  return temps;

}//float
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

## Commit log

2015-04-01 loaded current pcb files
    [Larvae_rig_skem.fzz, flypi_audio_usb1.fzz, flypi_banana1.fzz, flypi_bnc_usb1.fzz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]
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2015-04-13 added the stl and scad files to the repository
    [Fly-Pi manipulator_v4.scad, Fly-Pi manipulator_v4.stl, FlyPi_v20.scad, FlyPi_v20.stl]
2015-04-13 updated pcb design in flypi_bnc_usb1.fzz to the new design with relays
    [flypi_bnc_usb1.fzz]
2015-04-16 created a new version of the PCB. it uses relays for the peltier wiring and screw terminals to connect things. Also deleted 'Arduino/flyPi' folder, since it was a duplicate of the Arduino/FlyPi folde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
    [flypi_scew_terminals.fzz]
2015-05-29 updated the scad and stl files. now the model has a holder for camera filters
    [Fly-Pi manipulator_v5.scad, Fly-Pi manipulator_v5.stl, FlyPi_v21.scad, FlyPi_v21.stl]
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2015-08-26 created new PCB design file with screw terminals and h-bridge instead of relays
    [flypi_scew_terminals_L298N.fzz]
2015-08-26 created new PCB design file with screw terminals and relays
    [flypi_scew_terminals_relays.fzz]
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2015-10-29 uploaded a gerber version of the PCB that uses the l298n h-bridge
    [flypi_scew_terminals_L298N_contour.gm1, flypi_scew_terminals_L298N_copperBottom.gbl, flypi_scew_terminals_L298N_copperTop.gtl, flypi_scew_terminals_L298N_maskB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]
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2015-12-13 updated the wiring of the AD22100 temperature sensor, following the specshit
    [flypi_scew_terminals_L298N.fzz]
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2016-01-20 initial sketch for a new power supply.
    [flypi_new_power_supply.fzz]
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2016-04-04 PCB sketch using a linear voltage regulator to convert 12v to 5v and power the pi. This works, but it is a bad idea in principle, since a lot of energy is lost as heat, requiring massive heat dissipa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
    [flypi_linear_VR.fzz]
2016-04-04 created sketch for PCB using a switching regulator. Actually 3 of them. One for powering the pi, one of the Matrix, Ring and servo, and one for the two high powered out puts.
    [flypi_switching_VR.fzz]
2016-04-04 work on the PCB, corrected the inverted diodes and compeleted the schematics wiring.
    [flypi_switching_VR.fzz]
2016-05-29 clear old voltage regulator PCB
    [flypi_switching_VR.fzz]
2016-05-29 added new PCB .fzz file.
    [flypi_switching_VR_0_1.fzz]
2016-05-29 created gerber files for the new pcb
    [flypi_switching_VR_0_1_contour.gm1, flypi_switching_VR_0_1_copperBottom.gbl, flypi_switching_VR_0_1_copperTop.gtl, flypi_switching_VR_0_1_maskBottom.gbs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]
2016-06-02 update PCB and gerber: transistor type
    [flypi_switching_VR_0_1.fzz, flypi_switching_VR_0_1_copperBottom.gbl, flypi_switching_VR_0_1_copperTop.gtl, flypi_switching_VR_0_1_silkTop.gto]
2016-06-05 changed plug connection, trying to resolve the bug in the board
    [flypi_switching_VR_0_1.fzz]
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2016-08-26 Update to accommodate new pcb
    Tom's update to the 3d models to accomodate the new PCB
    [FlyPi_v29.scad]
2016-08-30 created BOM for the flypi
    [BOM.ods, BOM.xlsx]
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2016-09-14 added new pcb design with KiCad to git
    [flypi.kicad_pcb, flypi.sch]
2016-09-14 added pcb with KiCad
    [flypi-B.Adhes.gbr, flypi-B.CrtYd.gbr, flypi-B.Cu.gbr, flypi-B.Fab.gbr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]
2016-10-16 added schematics for electronics, python code and overall components
    [FlyPi_v29.scad]
2016-10-16 updated gerber files
    [flypi-B.Adhes.gbr, flypi-B.CrtYd.gbr, flypi-B.Cu.gbr, flypi-B.Fab.gbr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]
2016-10-16 updated BOM
    [BOM.ods, BOM.xlsx]
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2016-12-03 small changes to the files to be 3d printed
    [FlyPi_v29.scad]
2016-12-03 microfluidic chamber holder.
    [microfluidic_chamber_holder.scad]
2017-05-30 increased tolerance on print files to print with 0.8 nozzle
    [Fly-Pi manipulator_v5.scad, FlyPi_v29.scad]
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2017-06-05 repo clean uo, moving old and unused files to specific folders
    [BOM.ods, BOM.xlsx, Larvae_rig_skem.fzz, flypi-B.Adhes.gbr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]
2017-06-05 removing old files
    [BOM.ods, BOM.xlsx, Larvae_rig_skem.fzz, flypi_audio_usb1.fzz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]
2017-06-05 add new bill of materials
    [Bill_of_materials.ods, Bill_of_materials.xlsx]
2017-06-11 update camholder for picamera v2
    [FlyPi_v29.scad]
2017-07-27 created bill of materials with ali express suppliers
    [Bill_of_materials_aliexpres.ods]
2017-11-03 change to gerber file
    [flypi-B.Adhes.gbr, flypi-B.CrtYd.gbr, flypi-B.Cu.gbr, flypi-B.Fab.gbr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]
2017-11-03 update bill of materials
    [Bill_of_materials.ods, Bill_of_materials.xlsx, Bill_of_materials_aliexpress.ods, Bill_of_materials_aliexpress.xlsx]
2017-11-03 no change to 3D scad
    [FlyPi_v29.scad]
2017-11-03 deleted old aliexpress bom
    [Bill_of_materials_aliexpres.ods]
2017-11-03 individual parts added as stls
    [angled_stick.stl, base.stl, cam_mount.step, cam_mount.stl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]
2017-11-03 added stl plates containing organized parts
    [FlyPi_v26_plate1_Main a.stl, FlyPi_v26_plate2_Main b.stl, FlyPi_v26_plate3_Option Fluorescence.stl, FlyPi_v26_plate4_Option other.stl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]
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2017-11-16 Change for placement of parts into batches for printing (#20)
    * repo clean uo, moving old and unused files to specific folders
    * removing old files
    * add new bill of materials
    * update camholder for picamera v2
    * Fix README titles
    * Update README.md
    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
    [FlyPi_v29.scad]
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2017-11-19 update to pcb labels (corrected inverted values)
    [flypi-B.Adhes.gbr, flypi-B.CrtYd.gbr, flypi-B.Cu.gbr, flypi-B.Fab.gbr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]
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2018-03-09 found bug in gerbers
    [flypi-B.Adhes.gbr, flypi-B.CrtYd.gbr, flypi-B.Cu.gbr, flypi-B.Fab.gbr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]
2018-03-09 Prepare for kitspace (#22)
    * update to pcbs. Both SMD and new through hole. PCB is untested.
    * update 3d print files, and start the idea of having a library for common structures in the pieces
    * change to gerber files
    * update to pcb labels (corrected inverted values)
    * removed matrix commands from Arduino
    * major revision to python code. Reduced the number of recursive functions and data transmitted to arduino are now done only via flypiapp.py. Seems to have fixed protocols bugs and speeded up the Pel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
    [1-click-bom.tsv, BOM.ods, BOM_flypi.csv, BOM_flypi.ods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]
2018-03-09 Revert "Prepare for kitspace (#22)" (#23)
    This reverts commit 9aa00d109e1364754c2a30ef1fc76aca93cc7955.
    [1-click-bom.tsv, BOM.ods, BOM_flypi.csv, BOM_flypi.ods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]
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2018-03-09 Fix some issues with BOM
    [1-click-bom.tsv]
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2018-03-16 added some components, fixed some wrong parts
    [1-click-bom.tsv]
2018-03-19 fixed incorrect components
    [1-click-bom.tsv]
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2018-05-11 Update PCB to avoid errors when ordering from eurocircuits.com
    [1-click-bom.tsv, flypi-B.Adhes.gbr, flypi-B.CrtYd.gbr, flypi-B.Cu.gbr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]
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2018-08-16 fix stls
    [CameraHousing.stl, LED_Ring_LightDiffuser_print_in_white.stl, LED_Ring_holder.stl, LightFilter_Arm.stl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]
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2018-08-16 bring all updates from Prometheus development to original repo (#25)
    * small corrections to the timing address for LEDs
    * first change on the protocol class
    * added schematics for electronics, python code and overall components
    * updated gerber files
    * updated BOM
    * last chages tryig to fix protocol
    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
    [1-click-bom.tsv, 1-click-bom_old.tsv, BOM.ods, BOM.xlsx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]
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2018-08-16 bring all updates from Prometheus development to original repo (#25) (#26)
    * bring all updates from Prometheus development to original repo (#25)
    * see to have found the problem and solutio for the protocol app. System now is bidirectional. Pytho sends command and waits for done cofirmation from arduino
    * more development on the protocol class
    * arduino commit
    * app commit
    * protol commit
    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
    [1-click-bom.tsv, 1-click-bom_old.tsv, BOM.ods, BOM_flypi.csv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]
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2018-08-29 update bom (wrong connector on digikey)
    [1-click-bom.csv]
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2018-09-28 revert to 98f9291
    [CameraHousing.stl, LED_Ring_LightDiffuser_print_in_white.stl, LED_Ring_holder.stl, LightFilter_Arm.stl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]
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2018-11-10 correct csv rendering
    [1-click-bom.csv]
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2019-09-11 Files for issues 40-45 (#53)
    * Create sobianin
    * Delete sobianin
    * Create Manipulator_Zaxis_v2.STEP
    * Add files via upload
    * Rename RaspberryCase_Top.stp to RaspberryCase_Top_v2.stp
    * Version with hinges and improved closing system
    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
    [Manipulator_Zaxis_bolt.STEP, Manipulator_Zaxis_v2.STEP, PCBCase_Bot_v2.STEP, PCBCase_Top_v2.STEP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]
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2019-10-23 Updated LED holder (#55)
    * Lightweight version
    * Updated tolerances
    * Main bolt
    * Delete bolt_schlussel
    * Delete vise_v2.zip
    * Main bolt
    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
    [LED_holder_0.8.STEP, LED_holder_1.2_universal.STEP, LED_holder_rectangle_0.8.STEP, LED_holder_rectangle_1.2_universal.STEP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]
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2020-12-30 Addition of camera streaming and minor GUI enhancements (#71)
    * Update PetriDish_movable_jaw_screws_v2.STEP
    * Create Manipulator_Zaxis_T_holding_system
    * Shaft dimensions to use in designs
    * Update PCBCase_Bot_v2.STEP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
    [LightFilter_Arm_Cross2.STEP, LightFilter_Arm_Cross2.step, Manipulator_Zaxis_bolt.STEP, Manipulator_Zaxis_v2.STEP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]
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2021-05-12 fix misslabeling on board
    [flypi-B_Adhes.gbr, flypi-B_CrtYd.gbr, flypi-B_Cu.gbr, flypi-B_Fab.gbr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]

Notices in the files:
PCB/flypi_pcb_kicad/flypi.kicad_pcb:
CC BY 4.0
